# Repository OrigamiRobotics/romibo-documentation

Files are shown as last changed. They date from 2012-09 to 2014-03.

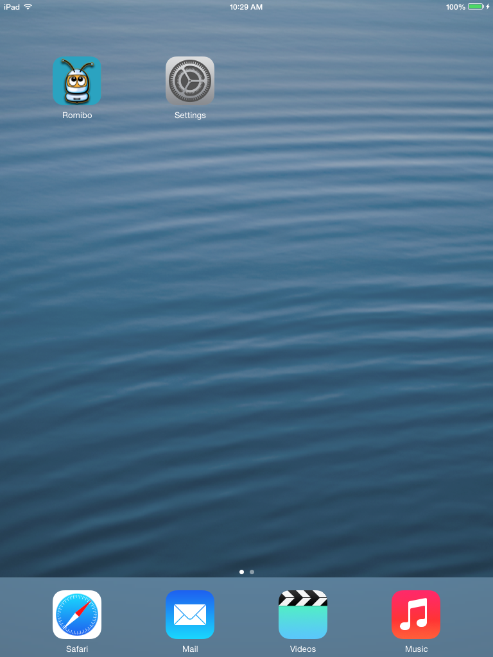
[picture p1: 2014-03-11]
iPad User Guide/Images/IMG_0007.PNG

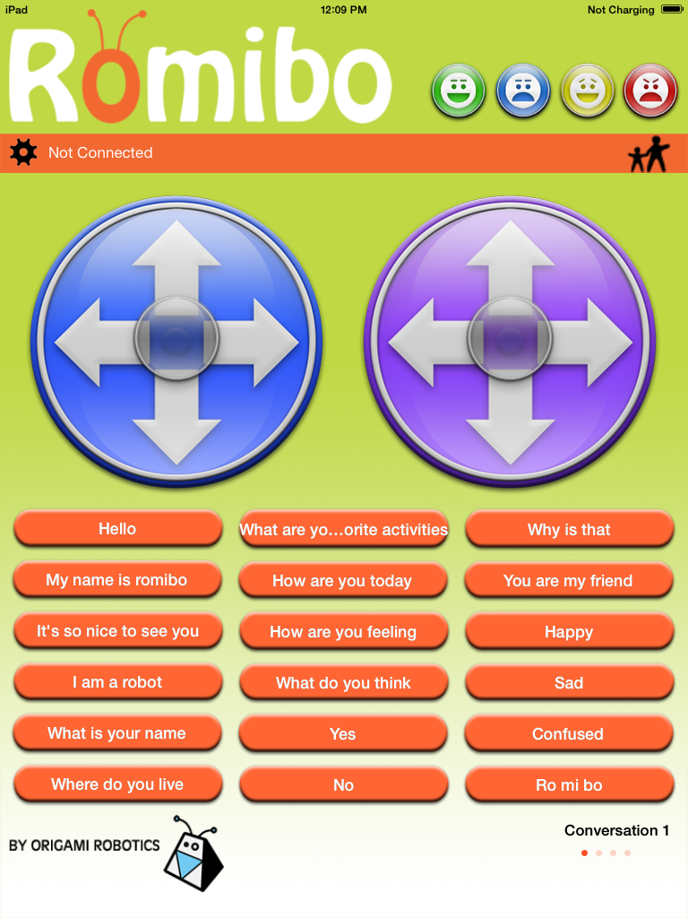
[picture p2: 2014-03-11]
iPad User Guide/Images/IMG_0014.PNG

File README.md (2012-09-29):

romibo-documentation
====================

Repository for documentation and printable materials for the Romibo robot

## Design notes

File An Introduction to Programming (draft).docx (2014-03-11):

An Introduction to Programming with

Romibo and Arduino:

by

Adam Warburton

The following will apply to all programs/sketches found in this tutorial:

// This is free software; you can redistribute it and/or modify

// it under the terms of the GNU General Public License as published by

// the Free Software Foundation; either version 2 of the License, or

// (at your option) any later version.

//

// This is distributed in the hope that it will be useful, but

// WITHOUT ANY WARRANTY; without even the implied warranty of

// MERCHANTABILITY or FITNESS FOR A PARTICULAR PURPOSE. See the

// GNU General Public License for more details.

//

// You should have received a copy of the GNU General Public License

// along with this file; if not, write to the Free Software Foundation,

// Inc., 51 Franklin St, Fifth Floor, Boston, MA 02110-1301 USA

// ##END_LICENSE##

/****************************************************************/

/****************************************************************/

What are Romibo and Arduino anyway?

An Arduino is a single-board microcontroller based on open-source hardware. Essentially an Arduino Board is a small computer that can be programmed to send and receive electrical signals. The Arduino is a computer, just like a laptop or desktop, but instead of being used for word-processing or web-surfing, it can be used in the design of robots and other devices. It also does not have anywhere near the processing power of a desktop computer, but is significantly cheaper and can interact with the physical world. An Arduino board can be programmed through a connection by USB to a computer.

Arduino Boards in themselves can only output weak electrical signals (5 Volts at an approximate maximum of 40 mA). Consequently, the board itself can do little more on its own than turn on LEDs. For this reason, Arduino boards are often connected to shields such as the Romibo Shield.

The Romibo Shield is a board that takes input from the Arduino Board and outputs the appropriate output voltages to the motors, servos, and other components on the Romibo Robot. The Romibo Shield also allows the Arduino to access input from numerous sensors including an accelerometer, microphone, IR sensor, two photo resistors and more. Table 1.1 contains the pins of the Arduino board with names for what they correspond to on the Romibo Shield.

Table 1.1 (modified from Romibo-Arduino-Pin-Assignments.xls by Garthz)

Arduino Pin | Rev3 Signal | Rev3 Function
A1 | RANGE | range sensor input
A2 | PHOTOLEFT | left photosensor input
A3 | PHOTORT | right photosensor input
A4 | PHOTOTOP | top photosensor input
A5 | MIC | microphone signal input
A6 | ENVELOPE | microphone envelope input
A7 | PHOTOFACE | face photosensor input
A8 | LCURRENT | left drive motor current feedback input
A9 | RCURRENT | right drive motor current feedback input
A10 | VINSENSE | battery input voltage input
D2 | FWDLEFT | left drive wheel IN1
D3 | REVLEFT | left drive wheel IN2
D4 | RED | red led PWM
D5 | MOTSLEEP | drive motor sleep output
D6 | MOTFAULT | drive motor fault input
D7 | FWDRT | right drive wheel IN1
D8 | REVRT | right drive wheel IN2
D9 | GRN | green led PWM
D10 | BLUE | blue led PWM
D13 | AUDIOPWM | experimental class-D audio amplifier PWM output
D18 | WIFITX | Serial1 data to WiFi module
D19 | WIFIRX | Serial1 data from WiFi module
D20 | SDA5V | I2C bus data
D21 | SCL5V | I2C bus clock
D28 | TOUCHLEFT | touch switch digital input
D29 | TOUCHBOT | touch switch digital input
D31 | TOUCHTOP | touch switch digital input
D34 | !DACS! | audio SPI chip select out
D35 | DASCK | bit-banged audio SPI clock out
D36 | DASDI | bit-banged audio API data out
D37 | !SPKSHDN | active-high enable for speaker amplifier
D40 | !SDCD! | SD Card detect
D45 | TILTBACK | servo PWM for rear neck servo
D46 | EYE | servo PWM for eyelid servo
D48 | IRIN | IR remote receiver input
D50 | SDDO | hardware SPI for SD Card
D51 | SDDI | hardware SPI for SD Card
D52 | SDSCLK | hardware SPI for SD Card
D53 | SDCS | digital I/O for master-mode SPI

Installing the Arduino IDE

Now that you’ve learned a little about the hardware, now would be a good time to start learning about the software. As stated earlier, the Arduino board can be programmed using a USB port. In order to begin programming with Arduino, you must first install the Arduino IDE on your computer. The Arduino IDE is available free of charge from http://arduino.cc/en/main/software

Please install the version that is appropriate for your device (Windows, Mac, Linux) and then restart your computer if necessary. After a successful installation, you will be able to start the program which should appear similar to that of Figure 1 below.

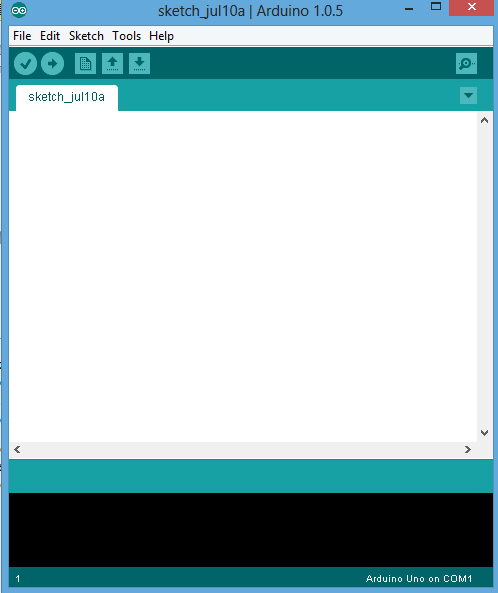
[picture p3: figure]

The first thing you will likely need to do is to change your IDE to work with the Arduino Mega. This is a fairly easy step, simply click Tools and then click on Board in the drop down menu and then choose the Arduino Mega 2560.

Then be sure to plug the robot into the USB port. Then click Tools and then Serial Port. Choose the only serial port available (example COM3). After that you should be ready to start programming.

Program 1:

Your First Sketch - Getting the Robot to Move

The Arduino Community refers to programs as Sketches. This section will guide you through the process of writing sketch that causes the robot to move forward, stop, then repeat. Arduino programming is based off of the open source programming language “Processing”. “Processing” shares similarities with other programming languages such as C++ and Java.

Every Arduino sketch must have two parts:

1. A setup function
2. A loop function

The setup function is self-explanatory. It sets up the Arduino Board. This function is run once and is important because it is used to tell the Arduino which pins to use for input and which to use for output.

The loop function is a function that is run after the setup function. Unlike the setup function however, the loop function will run an infinite number of times. It repeats or loops the function over and over again.

To write the outline of these bits of code, type the following:

void setup()

{

}

void loop ()

{

}

You will notice that the text changes colors. This is to help with programming as different types of code will be different colors. It is very important to keep the capitalization and punctuation the same. Brackets {} are not the same as parenthesis () .

Do not worry too much about the word “void” for now, we will discuss that later. The functions are void because there is no value of a number or character returned by them.

If you typed the code in correctly, it will appear like what is seen in Figure 2 below. Notice that the color of the text turned orange. The space in-between the brackets is where the code for each of the functions will go.

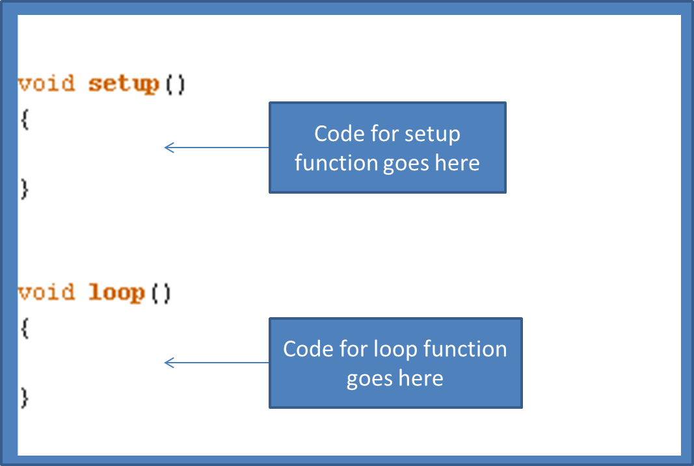
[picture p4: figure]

As mentioned earlier, the setup function will tell the Arduino which pins to use as input and output. For this particular program we will only be using output to the motors. There are four pins which will be important to us. These are Digital Pins 2, 5, 6, and 7.

Pins 2 and 7 tell the left and right motors to move forward respectively.

Pins 5 and 6 correspond to the motor sleep and motor fault switches.

Motor sleep and motor fault may sound foreign to you. Comparing them to every-day life, a person does not simply get into a car, put their foot on the gas and start moving. One has to first turn the key to start the car. One also has to shift gears from park to drive. The motor sleep switch will need to be triggered to essentially start the motor (turn the key). The motor fault switch can be compared to putting the car in drive. To enable these pins, the corresponding pins will first need to be declared as output. To do this, type the following code into the setup function (between the brackets {} after void setup() ).

pinMode (2, OUTPUT);

pinMode (5, OUTPUT);

pinMode (6, OUTPUT);

pinMode (7, OUTPUT);

Note that there is a semicolon “;” after each line. This semicolon tells the compiler (the program on your computer in which you typed this) that you have typed a complete statement. The semicolon is similar to punctuation in speech. Once you finish a statement, you end with a period. Otherwise, sentences would be run-on jumbled messes of difficult to understand nonsensical word jumble that is really really really long, confusing, hard to decipher, and did I mention confusing because if I didn’t I should have.

All joking aside, look at the statements that were typed. Each one of them has the pinMode function. This function tells Arduino that the pin number that follows should be either an input or an output. The number within parenthesis is followed by a comma and then the word INPUT or OUTPUT in all capital letters. The ending parenthesis is then added followed by a semicolon.

Now that we have declared the pins to be outputs, it would be good to set the MOTSLEEP and MOTFAULT pins to output a signal so that we have essentially turned the key to our motors and set them to drive. To do this, type the following code into the setup function (between the brackets) but after the code that set the pins to be outputs.

digitalWrite (5, HIGH);

digitalWrite (6, HIGH);

Again, don’t forget the semicolons! Also, please make sure that the capitalization is correct.

What you’ve just typed is the digitalWrite function. This function is digital because it is outputting to a digital pin (Arduino also has analog pins which will be discussed later). A digital pin is either on or off. To turn a pin on, it is written to as HIGH for a high signal being sent. To turn a pin off it will be sent a LOW signal. Just like the pinMode function, the number used in-between the parenthesis corresponds to the pin that the data is being sent to.

Now that you have successfully set up your Arduino, it’s time to move on to the loop function.

To get the robot to move, you will use the same digitalWrite function that you used to turn the MOTFAULT AND MOTSLEEP switches on. See if you can write these bits of code on your own for pins 2 and 7 in the loop function.

The next function you will need to know about is the delay function. The Arduino board will move through the code you type at an incredibly rapid rate (Thousands of lines per second). To get the board to slow down, you will need to tell it to wait. The delay function has one parameter (value within parenthesis) that tells it how many milliseconds to delay the program. Consequently to have the board wait one second or 1000 milliseconds you should type the function

delay (1000);

This will cause the Arduino to wait a full second before moving onto any code that follows.

As of now, you should have a loop that turns the motors on, waits a second, and then turns the motors on again, then waits another second and so on. But this isn’t especially useful if you want the robot to take a pause for a while. Therefore, you will need to tell the motors to turn off as well. This can be done with the digitalWrite function. Only this time, you will be using LOW instead of HIGH.

digitalWrite (2, LOW);

digitalWrite (7, LOW);

This will turn the motors off after a one second delay. However, the motors will immediately be turned back on again when the loop function repeats. Therefore you should add another delay of a time of your choosing after turning the motors off.

Overall, your program should look something like the following in the compiler.

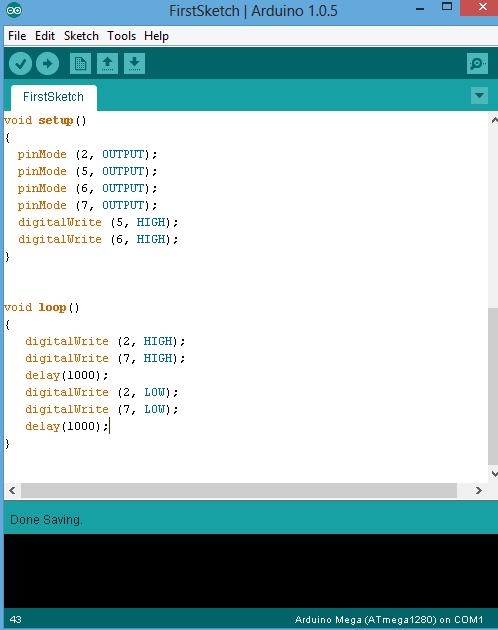
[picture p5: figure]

To check if your program was written with proper syntax, click on the check mark at the top of the program. This will compile your program. This means that it will translate the code you typed into something that can be understood by the Arduino board. If the code is written so that the computer can understand it, the compiler will show a “done compiling” message. Otherwise the compiler will inform you of errors.

Just because a program compiles does not mean it will do what you want it to do. To check to see if your sketch works, you will need to upload it to your Romibo. To do this, connect your Romibo to your computer using a USB cable. Then click on the upload arrow next to the check mark you just used to compile your sketch.

(Depending on your machine, you may have some errors the first time you connect the robot. For help connecting your computer to the Arduino, there are multiple pages on the internet that can be found from your favorite search engine.)

If everything was successful, you will see a message that says “done uploading”. You may now unplug your robot and set it on the floor (away from any obstacles). Turn on the robot and see if it behaves as you expected.

Did the robot do what you expected?

Hopefully it did. If not, there are a few possible reasons it did not. If the robot did not move at all, the motors may not be properly connected or the code may need to be adjusted. The batteries in the robot may also need to be replaced.

Did your robot move backward? If so, the motors were installed backward. This isn’t as huge of a problem as you might expect. One solution is to open the robot and move the motors. The other is to simply alter your program. In the code you can replace the pin numbers you used for the motors to move forward (2 and 7) with the ones for the motors to move in the opposite direction (3 and 8). This is a lot easier than actually opening up the robot, but you may want to note this somewhere if you plan on keeping the robot this way.

Program 2:

Responding to Input:

In this section, you will learn how to make the Romibo Robot respond to input from its touch sensors. The example program will have the robot turn in circles but change direction each time it is triggered by a touch sensor.

As can be seen from the previous table of Arduino pins (table 1.1), the pins for the touch sensors are numbered 28, 29, 30, and 31. Since these pins will be inputting data into the Arduino, these pins will need to be declared as INPUT using the pinMode function.

pinMode ( pinNumber, INPUT);

Make sure to declare all four of these pins in the setup function. To read from a pin you will use the digitalRead() function. The digitalRead function includes one parameter, the pin number that is being read.

digitalRead(28) will return HIGH if the touch sensor/ button is not being pressed and LOW if the button is being pressed. The reason for this is that the button grounds the connection whenever the two pieces of metal come in contact. Simply writing digitalRead(28) as a statement in your code though will do very little. To make the input change something, you will need to instruct your Arduino to make a decision.

One way of allowing your Arduino Board to make a choice is with the “if statement”. An “if statement” asks if something is true, and if it is will do something else. A basic setup of the way to write this “if statement” using normal everyday decisions is:

if (you have a dog)

{

walk it everyday

}

As you can see from the above pseudo-code, the text in the parenthesis is what is being checked to see if it is true. The text in the brackets is what is being done if the checked statement was true. It would not make sense to walk a dog that does not exist.

To check multiple statements you will need to connect the statements with either an || (or) or an && (and). The || or && is text that is understood by the compiler. In pseudo-code

if (you have a dog || you have a cat)

{

put food out

}

This bit of pseudo-code tells you that if you have a dog or if you have a cat that you should put food out for it. You can also give commands for when something isn’t true. For example

if (you have a dog || you have a cat)

{put food out}

else

{

consider getting a pet

}

This “if -else statement” allows the program to choose from two different responses. The “else” is performed whenever the previous if was not performed. From these examples, one “if statement” you will want to form looks something like this:

if (digitalRead(28) == LOW || digitalRead(29) == LOW || digitalRead(30) == LOW || digitalRead(31) == LOW)

{

}

This code will check to see if any of the buttons have been pressed. If so, the code that follows in the brackets will be performed. Notice that there are 2 equal signs to test if something is equal. This is important. One equal sign will actually make something equal to something else. The something that is referred to is a variable. Since this program will be causing the robot to choose between turning right and turning left, we will need to declare a variable to decide which direction the robot is turning.

To declare a Boolean variable named TurningRight that is either true or false we write

boolean TurningRight;

Be sure to put this bit of code at the very top of your Sketch. Being before any of the functions will allow this variable to be accessed anywhere in the sketch. We could have named this variable anything we like (provided it starts with a letter and has no spaces or illegal symbols). However, TurningRight is descriptive of what should be true or false.

To set a variable to some value, you use one equal sign. If you want the robot to turn right at the start of the program, put this bit of code into the setup loop.

TurningRight = true;

This will set the variable to true. Simply doing this though will not cause your robot to turn right. You will have to cause the motors to turn after testing the TurningRight variable. To cause the robot to turn right, you will actually have to tell the left motor to move forward. This is because the right wheel will effectively remain stationary. If you turn to the right yourself, you will notice that you pivot on your right foot and move your left foot around. This is how the robot will have to move as well. This can be visualized with the following image.

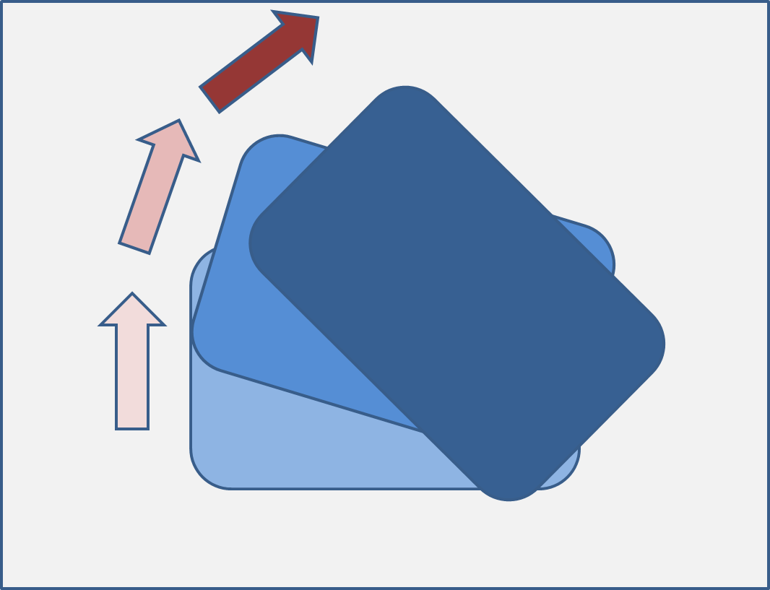
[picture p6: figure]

Given this information about variables, if statements, and input, you should be able to write a complete working sketch that will make the robot change direction when a button is pressed. Give it a try on your own and upload it to the robot. Remember that the left motor forward is pin 2 and the right motor forward is pin 7. If you need help, try searching the internet. For a complete program see the next page.

Hint: “if-else statements” can go within other “if-else statements”

//SecondSketch_Input_

boolean TurningRight;

void setup()

{

TurningRight = true;

pinMode (2, OUTPUT);

pinMode (5, OUTPUT);

pinMode (6, OUTPUT);

pinMode (7, OUTPUT);

digitalWrite (5, HIGH);

digitalWrite (6, HIGH);

pinMode (28, INPUT);

pinMode (29, INPUT);

pinMode (30, INPUT);

pinMode (31, INPUT);

}

void loop()

{

if (digitalRead(28) == LOW || digitalRead(29) == LOW || digitalRead(30) == LOW || digitalRead(31) == LOW)

{

if (TurningRight == true)

{

TurningRight = false;

digitalWrite (2, LOW);

digitalWrite (7, HIGH);

delay (250); //This delay will keep the button from being checked to quickly

}

else

{

TurningRight = true;

digitalWrite (2, HIGH);

digitalWrite (7, LOW);

delay (250); //This delay will keep the button from being checked to quickly

}

}

}

Program 3:

Analog Input, Variable Types, and the Serial Monitor

Up until now, you’ve been using entirely digital input and output. These digital inputs are either completely on or off. However, there is another type of input/output called analog. Use of analog allows there to be a range of values between on and off.

A sensor that is ideal for showing analog input is the photo resistor. If you are unfamiliar with electricity, resistors exist in electrical circuits in order to impede the flow of electrons. Resistors can be thought of as small tunnels that electrons have to pass through. The electrons have to move slower in the same way that cars move slower when entering a tunnel. A photo resistor is a resistor whose resistance (essentially the size of the tunnel) changes whenever a light is shining onto the resistor. A photo resistor’s resistance is less whenever more light is being shined on it. This is because the light essentially loosens the electrons from the material, allowing them to flow easier. (The actual explanation is slightly more complicated. This idea will give you a general idea of the concept however).

The two photo resistors on the front of the Romibo are connected to Analog Pins 2 and 3 for left and right respectively. You may be wondering, “isn’t pin 2 taken already”. The answer is no, digital pin 2 is taken for a motor but analog pin 2 is used for the left photo resistor.

To receive data from the photo resistor, you will need to store it somewhere. Just as you declared a Boolean variable in the last programming exercise, you will also need to declare a variable to store this data. However, this data will not be true/false. The data you will be receiving will be a number. There are multiple ways of storing numbers using Arduino.

Abbreviation | Name | Meaning
int | Integer | Stores integer variables from -32,768 to 32,767
long | Long | Stores larger integer values from -2,147,483,648 to 2,147,483,647
double | Double | Stores values with a decimal point.

The number we will be storing for each photo resistor reading will be an integer. To declare these values you can type:

int leftPhotoReading;

int rightPhotoReading;

Integer values are helpful in storing readings from analog input. They can also be used to save time in remembering values you’d rather not memorize. For example, you’ve been writing to a digital pin 7 to trigger one of the motors for a while now. Instead of writing digitalWrite(7, HIGH), you could define a variable such as FWDRT to 7 and instead type digitalWrite(FWDRT, HIGH). To declare a constant, just type const before the name of the variable and put an equal sign after it followed by the value you want it declared to. For example:

const int FWDRT = 7;

While it is not required, constants are typically typed in all capital letters. To change a non-constant variable, you just type the name of the variable, an equal sign, and then the value you want the variable to change to. The great part about this is that you can make a variable equal to the value returned from a function or a mathematical statement. For example,

int PHOTOLEFT = 2*1-0; // * means multiplication

int PHOTORIGHT = 1 + 4/2;

The compiler will follow order of operations, just like in math class. Therefore the above code will set PHOTOLEFT to 2 and PHOTORIGHT to a value of 3. Instead of assigning values to our reading variables, it will be more useful to allow them to actually read in data from an analog input. To read analog input, use the function analogRead(pin_number). For our code, we will use

leftPhotoReading = analogRead(PHOTOLEFT);

rightPhotoReading = analogRead(PHOTORIGHT);

The analogRead( ) function will return a value from 0 to 1023. For photo resistors, the brighter the light shining on the photo resistor, the lower the number returned.

To see what numbers are being returned by your robot you can use a tool called the Serial Monitor. To have your robot return data back to your computer, you will have to include a few lines of code. In your setup loop please include

Serial.begin(9600);

For your loop() please include the following. Be sure that you declare all of the necessary variable and set the correct pinMode for all pins. For a working program see Program3 SerialPrint Example.

leftPhotoReading = analogRead(PHOTOLEFT);

rightPhotoReading = analogRead(PHOTORIGHT);

Serial.print("leftPhotoReading ");

Serial.println(leftPhotoReading);

Serial.print("rightPhotoReading ");

Serial.println(rightPhotoReading);

delay(300);

After successfully compiling your program, upload it to your robot. Do not unplug the USB port. Instead, click on Tools at the top of your Arduino IDE. Then click on Serial Monitor. Be sure that AutoScroll is checked, both NL & CR is chosen from the first drop down list, and 9600 baud is selected. Cover and shine lights on the photo resistors to see how the data responds. Look back at the code you entered to see how the Serial.print and Serial.println functions work.

Notice that parenthesis output the exact text and that variable names output the variable value.

//Program3 SerialPrint Example

int leftPhotoReading;

int rightPhotoReading;

const int PHOTOLEFT = 2;

const int PHOTORIGHT = 3;

void setup()

{

Serial.begin(9600);

}

void loop()

{

leftPhotoReading = analogRead(PHOTOLEFT);

rightPhotoReading = analogRead(PHOTORIGHT);

Serial.print("leftPhotoReading ");

Serial.println(leftPhotoReading);

Serial.print("rightPhotoReading ");

Serial.println(rightPhotoReading);

delay(300);

}

Now, that you’ve seen how the analogRead function works with photo resistors, you are ready to start making more complex programs. Instead of the program you made in the last section that has the robot change direction by a button press, try making one that has the robot follow a light. Review the section of if-else statements if need be. The following are available to produce true or false values. You have seen == before, the other should be easy to infer.

> greater than < less than >= greater than or equal to <= less than or equal to == equal to

Between, these comparisons and the ability to use +,-,*,and / to add, subtract, multiply, and divide, you should be able to make your robot do more complex motions. Example code of a robot following a light can be found on the following page. Try to create your own or edit the one provided to fine tune your program.

//Program3 ChaseLight Example

int leftPhotoReading;

int rightPhotoReading;

const int PHOTOLEFT = 2;

const int PHOTORIGHT = 3;

const int FWDRT = 7;

const int FWDLEFT = 2;

void setup()

{

pinMode (2, OUTPUT);

pinMode (5, OUTPUT);

pinMode (6, OUTPUT);

pinMode (7, OUTPUT);

digitalWrite (5, HIGH);

digitalWrite (6, HIGH);

}

void loop()

{

leftPhotoReading = analogRead(PHOTOLEFT);

rightPhotoReading = analogRead(PHOTORIGHT);

if(leftPhotoReading < rightPhotoReading - 30)

{

digitalWrite(FWDRT, HIGH);

digitalWrite(FWDLEFT, LOW);

}

else if(rightPhotoReading < leftPhotoReading - 30)

{

digitalWrite(FWDRT, LOW);

digitalWrite(FWDLEFT, HIGH);

}

else

{

digitalWrite(FWDRT, HIGH);

digitalWrite(FWDLEFT, HIGH);

}

}

Program 4:

Analog Output, Lighting, Changing Speeds, and Loops

In the last section, we covered Analog Input which had a range of values from 0 to 1023. Analog output is similar but it will only be able to use values from 0 to 255. Consequently, an effective way to convert from one to the other is to divide by four. Using the value of 255 will cause the pin to be constantly on while 0 will make it constantly off. A value in between will cause the pin to be on a fraction of the time. The function to use for analog output is

analogWrite(pinNumber, value); //where ‘value’ is from 0 to 255

This function will typically be used in void loop() section of the code. Analog Output is an effective way to cause the motors to change speeds or to cause the LED lights to appear to be at different brightness levels. The Romibo has a Tri-color LED which creates the color in the antenna. While the LED is tri-color it can actually create any other color from its three colors (red, green, and blue). You are likely familiar with the three primary colors when painting, red, yellow, and blue. From these three paint colors you can mix any other color of paint. Light is similar but the three primary colors are different. For light, they are red, green, and blue. These same three colors are the ones used in LCD TVs and monitors to create every color on the screen.

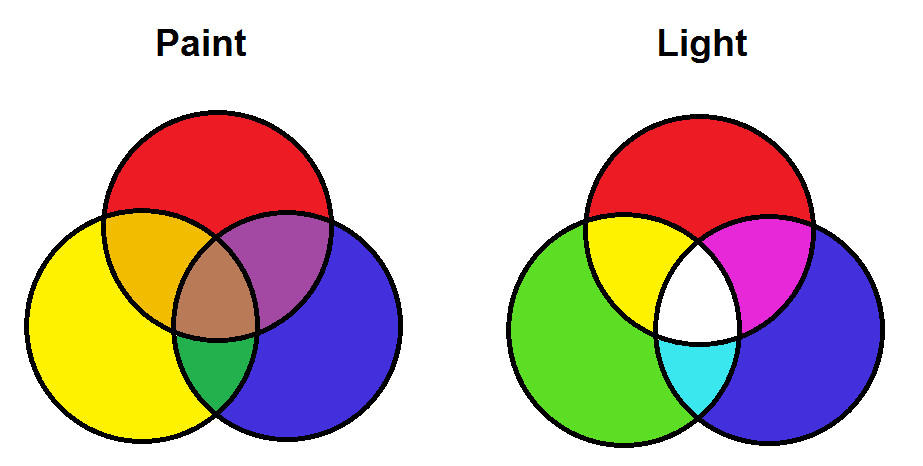
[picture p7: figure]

The reason for the difference in the primary colors is that when you add paint colors together, you are actually subtracting out the wavelengths of light that are reflected. When you add more light to something, you are adding the colors together. As you add more paint color, the color gets darker. But when you add more light, everything gets lighter.

The pins for the Red, Green, and Blue parts of the LED on Romibo are 4, 9, and 10 respectively. While these are considered digital pins, they will still accept a command from analogWrite(pin, val);

If you plan on changing the value sent to a pin gradually, it will likely be beneficial to use something called a loop in programming. You have actually been using an infinite loop all along with the loop function. However, these loops will be performed within your code if some condition is true. The three loops introduced are found in other languages such as C++ and javascript as well.

The first loop we may use is a “for” loop. A for loop will loop a certain number of times. Rather it will repeat a particular set of code a certain predetermined number of times. If you wanted to make the LED’s Blue output gradually increase, you could use the following code.

for (int i = 0; i < 254; i++)

{

analogWrite(10, i); //code that is repeated each time

delay (4);

}

In this example, the variable ‘i’ is declared inside of the parenthesis. It will continue as long as the next statement is true (i < 254;). The update condition is then placed after that (i++ means that ‘i’ will increase by one each time). After parenthesis, the code that is repeated follows inside brackets (just like the if statement). Notice, that since ‘i’ increases each time the loop repeats, that the value written to the blue led will increase each time the loop repeats. This variable ‘i’ will not exist after the for loop as it is a local variable.

This loop is very helpful, but what if you don’t know how many times you want the loop to repeat? You could make a loop that repeats as long as an input button is pressed for instance, or as long as the photo resistor receives light of a certain brightness. A good loop to use would be a while loop.

int outputValue = 0;

while (analogRead(PHOTORIGHT) > 400)

{

outputValue = analogRead(PHOTORIGHT)/4;

analogWrite(10, outputValue); //code that is repeated each time

}

Notice that the code will repeat until analogRead(PHOTORIGHT) is less than or equal to 400. This could be dangerous to use if the value will never fall that low. The value output to the Blue LED pin will change constantly but no other code in your program will be executed until you leave the while loop.

A loop that is similar to the while loop but will be executed at least one time is the do-while loop.

int outputValue = 0;

do

{

outputValue = analogRead(PHOTORIGHT)/4;

analogWrite(10, outputValue); //code that is performed at least once

} while (analogRead(PHOTORIGHT) > 400);

This loop will perform the code inside the brackets at least once regardless of whether analogRead(PHOTORIGHT) is greater than 400 or not. If that is false, the program will continue on as normal, having updated the Blue LED pins value. An example program that will let you see the colors of light changing follows. Try it on your Romibo and edit it to your liking.

//Antenna Color Shift

int timer = 0;

const int RED = 4;

const int BLUE = 10;

const int GRN = 9;

void setup()

{

pinMode (RED, OUTPUT);

pinMode (GRN, OUTPUT);

pinMode (BLUE, OUTPUT);

}

void loop()

{

timer = 0;

while (timer < 254)

{

analogWrite(RED, timer);

timer++;

delay (4);

}

for (int i = 0; i < 254; i++)

{

analogWrite(RED, timer - i);

analogWrite(BLUE, i);

delay (4);

}

timer = 0;

do

{

analogWrite(BLUE, 254 - timer);

analogWrite(GRN, timer);

timer++;

delay(4);

}while (timer < 253);

while (timer > 0)

{

analogWrite(GRN, timer);

timer--;

delay(3);

}

}

Other Example Programs:

This manual is a work in progress. There are more lessons to come. Some other example programs follow if you’d like to experiment with them.

//Read IR Values

const int IRIN = 48;

const int RED = 4;

const int BLUE = 10;

const int GRN = 9;

int highPulse;

int lowPulse;

const int RESOLUTION = 20;

int pulses[60][2];

long useconds;

int currentPulse;

void setup(void)

{

pinMode (RED, OUTPUT);

pinMode (GRN, OUTPUT);

pinMode (BLUE, OUTPUT);

pinMode (IRIN, INPUT);

Serial.begin(9600);

Serial.println("Printing IR delays");

}

void loop(void)

{

currentPulse = 0;

while (digitalRead(IRIN))

{

while (digitalRead(IRIN))

{

useconds = useconds + RESOLUTION;

delayMicroseconds(RESOLUTION);

}

pulses[currentPulse][0] = useconds;

useconds = 0;

while (!digitalRead(IRIN))

{

useconds = useconds + RESOLUTION;

delayMicroseconds(RESOLUTION);

if (useconds > 4800)

break;

}

pulses[currentPulse][1] = useconds;

currentPulse++;

}

Serial.println("New Data Set");

for (int i = 0; i < currentPulse; i++)

{

Serial.print(pulses[i][0]);

Serial.print(" ");

Serial.print(pulses[i][1]);

Serial.println(" ");

}

//Respond to IR Values

//Works with Sanyo Remote to trigger lights

const int IRIN = 48;

const int RED = 4;

const int BLUE = 10;

const int GRN = 9;

int highPulse;

int lowPulse;

const int RESOLUTION = 20;

int pulses[60][2];

long useconds;

int currentPulse;

boolean lighton = false;

void setup(void)

{

pinMode (RED, OUTPUT);

pinMode (GRN, OUTPUT);

pinMode (BLUE, OUTPUT);

pinMode (IRIN, INPUT);

Serial.begin(9600);

Serial.println("Printing IR delays");

}

void loop(void)

{

currentPulse = 0;

while (digitalRead(IRIN))

{

while (digitalRead(IRIN))

{

useconds = useconds + RESOLUTION;

delayMicroseconds(RESOLUTION);

}

pulses[currentPulse][0] = useconds;

useconds = 0;

while (!digitalRead(IRIN))

{

useconds = useconds + RESOLUTION;

delayMicroseconds(RESOLUTION);

if (useconds > 4800)

break;

}

pulses[currentPulse][1] = useconds;

currentPulse++;

}

Serial.println("New Data Set");

for (int i = 0; i < currentPulse; i++)

{

Serial.print(pulses[i][0]);

Serial.print(" ");

Serial.print(pulses[i][1]);

Serial.println(" ");

}

for (int i = 0; i < 90; i++)

{

if (pulses[i][0] == 840 && pulses[i+1][0] == 840 && pulses[i+2][0] == 840 && pulses[i+3][0] == 840 && pulses[i+4][0] == 1740 && pulses[i+5][0] == 840);

{

lighton = !lighton;

if (lighton)

{

digitalWrite(GRN, HIGH);

digitalWrite(RED, LOW);

digitalWrite(BLUE, LOW);

}

else

{

digitalWrite(GRN, LOW);

digitalWrite(RED, LOW);

digitalWrite(BLUE, LOW);

}

break;

}

if (pulses[i][0] == 840 && pulses[i+1][0] == 840 && pulses[i+2][0] == 840 && pulses[i+3][0] == 860 && pulses[i+4][0] == 840 && pulses[i+5][0] == 1720);

{

lighton = !lighton;

if (lighton)

{

digitalWrite(GRN, LOW);

digitalWrite(RED, HIGH);

digitalWrite(BLUE, LOW);

}

else

{

digitalWrite(GRN, LOW);

digitalWrite(RED, LOW);

digitalWrite(BLUE, LOW);

}

break;

}

if (pulses[i][0] == 1720 && pulses[i+1][0] == 1740 && pulses[i+2][0] == 1720 && pulses[i+3][0] == 1740);

{

lighton = !lighton;

if (lighton)

{

digitalWrite(GRN, LOW);

digitalWrite(RED, LOW);

digitalWrite(BLUE, HIGH);

}

else

{

digitalWrite(GRN, LOW);

digitalWrite(RED, LOW);

digitalWrite(BLUE, LOW);

}

break;

}

}

}

For some, programming can easily be learned from simply reading over someone else’s work. The following program was written with the QoLT young scholars program. Try uploading the code to your robot to see how it behaves. Refer back to the code to see why it does each behavior. Be sure to touch each of the touch sensors.

// From_Scratch_Demo

// Anna + Jason + Adam

//These includes include other files for programming.

//These files tell the arduino how to handle functions that involve a timer or servos.

#include <Timer.h>

#include <Servo.h>

//The following are variables.

//int stands for integer. The name that follows is the name of the variable.

//These variables can hold integer values.

int inversedistance;

int beat1time;

int beat2time;

int beat3time;

int beat4time;

int beataveragetime;

//The const before the int means that the variable is a constant

//These values will not change while the program is running.

const int FWDLEFT = 2; //These Numbers are the numbers of the pins on the arduino board that connect to the motors.

const int REVLEFT = 3; //For Example, sending a signal to REVLEFT (pin 3) will cause the Left motor to move in reverse.

const int FWDRT = 7; //It is not necessary to declare these constants if you remember the pins. But since that would be difficult the variables can stand in place for the pin numbers later.

const int REVRT = 8;

const int RANGEPIN = 1;

//A boolean variable is either true or false; The value can be declared initially with =

//The robot will not start dancing until code instructs it to do so.

boolean IsDancing = false;

int BeatsDanced = 0;

boolean lastButton = true;

boolean motorOn = false;

//A long is also an integer but it is for larger numbers.

//Since time is measured in milliseconds, these values can become quite large. Therefore long is more appropriate than int.

long startTime;

//Servo is for use with Servo Motors. These will move to a particular position.

Servo ForwardServo;

Servo BackwardServo;

//This is a function declaration. void means that the variable has no parameters

//It is neither true, false, a number, or a letter. It is nothing really.

void DanceFunction (void);

//This setup function is required for use with arduino.

//Anything that follows in the squiggly brackets {} will be performed when the robot is first turned on.

void setup(void)

{

Serial.begin(9600);

ForwardServo.attach(44);

BackwardServo.attach(45);

//lets motors work

pinMode (5, OUTPUT);

digitalWrite (5, HIGH);

pinMode (6, OUTPUT);

digitalWrite (6, HIGH);

delay (1000);

}

//This loop function is also required for use with arduino

//After setup is performed, loop will be performed.

//The loop function will repeat over and over again until the robot is turned off.

void loop()

{

if (digitalRead (28) == LOW)

{

ForwardServo.writeMicroseconds(2000); //tilts head forward

BackwardServo.writeMicroseconds(2000);

delay(1000);

ForwardServo.writeMicroseconds(1000); //tilts head backward

BackwardServo.writeMicroseconds(1000);

delay(1000);

ForwardServo.writeMicroseconds(1500); //tilts head to center

BackwardServo.writeMicroseconds(1500);

delay(500);

}

if (digitalRead (29) == LOW)

{

digitalWrite (FWDLEFT, HIGH);

delay (1000);

digitalWrite (FWDLEFT, LOW);

digitalWrite (REVLEFT, HIGH);

delay (1000);

digitalWrite (REVLEFT, LOW);

}

if (digitalRead (31) == LOW)

{

digitalWrite (FWDRT, HIGH);

delay(1000);

digitalWrite (FWDRT, LOW);

digitalWrite (REVRT, HIGH);

delay(1000);

digitalWrite (REVRT, LOW);

}

//DanceFunction();

if (digitalRead(30) == LOW && lastButton == true)

{

startTime = millis();

digitalWrite (FWDLEFT, HIGH);

digitalWrite (FWDRT, HIGH);

ForwardServo.writeMicroseconds(2000); //tilts head forward

BackwardServo.writeMicroseconds(2000);

lastButton = false;

delay(150);

motorOn = true;

}

if ((digitalRead(30) == LOW && lastButton == false) || (millis() - startTime >= 30000))

{

digitalWrite (FWDLEFT, LOW);

digitalWrite(FWDRT, LOW);

lastButton = true;

delay(150);

motorOn = false;

}

if (motorOn == true && analogRead(RANGEPIN) >= 260)

{

digitalWrite(FWDLEFT, LOW);

digitalWrite(FWDRT, LOW);

if (millis() % 2)

{ digitalWrite(REVLEFT, HIGH);

digitalWrite(REVRT, HIGH);

delay(200);

digitalWrite(REVLEFT, LOW);

delay(1000);

digitalWrite(REVRT, LOW);

}

else

{

digitalWrite(REVLEFT, HIGH);

digitalWrite(REVRT, HIGH);

delay(200);

digitalWrite(REVRT, LOW);

delay(1000);

digitalWrite(REVLEFT, LOW);

}

}

if (motorOn == true && analogRead(RANGEPIN) <=230)

{

digitalWrite(FWDLEFT, HIGH);

digitalWrite(FWDRT, HIGH);

}

Serial.println(analogRead(RANGEPIN));

inversedistance = analogRead(RANGEPIN);

if (inversedistance >= 230)

{

ForwardServo.writeMicroseconds(1000); //tilts head backward

BackwardServo.writeMicroseconds(1000);

}

if (inversedistance <=210)

{

ForwardServo.writeMicroseconds(1500); //tilts head to center

BackwardServo.writeMicroseconds(1500);

}

}

void DanceFunction (void)

{

if (digitalRead (30) == LOW)

{

beat1time = millis();

delay (180);

for (int i=0; i < 1000; i++)

{

if (digitalRead(30) == LOW)

{

beat2time = millis();

i=1000;

}

delay (2);

}

delay (180);

for (int i=0; i < 1000; i++)

{

if (digitalRead(30) == LOW)

{

beat3time = millis();

i=1000;

}

delay (2);

}

delay (180);

for (int i=0; i < 1000; i++)

{

if (digitalRead(30) == LOW)

{

beat4time = millis();

i=1000;

delay(180);

}

delay (2);

}

beataveragetime = (((beat2time - beat1time) + (beat3time - beat2time) + (beat4time - beat3time))/3);

IsDancing = true;

}

if (IsDancing)

{

ForwardServo.writeMicroseconds(1800); //tilts head forward

BackwardServo.writeMicroseconds(1800);

digitalWrite (FWDLEFT, HIGH);

digitalWrite (REVRT, HIGH);

delay(beataveragetime/6);

digitalWrite (FWDLEFT, LOW);

digitalWrite (REVRT, LOW);

delay(beataveragetime/6);

delay(beataveragetime/3);

ForwardServo.writeMicroseconds(1200); //tilts head backward

BackwardServo.writeMicroseconds(1200);

digitalWrite (FWDRT, HIGH);

digitalWrite (REVLEFT, HIGH);

delay(beataveragetime/6);

digitalWrite (FWDRT, LOW);

digitalWrite (REVLEFT, LOW);

delay(beataveragetime/6);

BeatsDanced++;

if (BeatsDanced >= 16)

{

BeatsDanced = 0;

IsDancing = false;

}

}

}

I hope that you’ve enjoyed this introduction to programming with Romibo and Arduino. There is always more to learn. For other code, check out Romibo’s github page. For information on programming with Arduino, there are numerous resources on Arduino.cc/en

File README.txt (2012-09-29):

README.txt
September 28, 2012

This folder contains documentation on the Romibo(R) robot, a
social robot designed for therapy, education and fun.

The Romibo Project is a Carnegie Mellon University research project and a
community co-development project managed by Origami Robotics LLC.  More project
information can be found at http://www.romibo.org. Romibo is a registered
trademark of Origami Robotics LLC.

================================================================ 

The mechanical design drawings were created by Garth Zeglin using the commercial
CAD program SolidWorks 2010 Standard.

The CAD model primarily includes the flat snap-fit plastic parts of the robot
structure.  These are suitable for laser-cutting from flat double-smooth ABS
plastic of nominal 1/8" thickness.  This material has an actual thickness of
about 0.118 inches, reflected in the slot widths in the structure.

All mechanical files are available under the terms of the GNU General Public
License Version 2, the text of which appears in
GNU-General-Public-License-Version-2.txt.

The full notice for each file is as follows:

    Copyright (C) 2012 Carnegie Mellon University.

    This program is free software; you can redistribute it and/or modify
    it under the terms of the GNU General Public License as published by
    the Free Software Foundation; either version 2 of the License, or
    (at your option) any later version.

    This program is distributed in the hope that it will be useful,
    but WITHOUT ANY WARRANTY; without even the implied warranty of
    MERCHANTABILITY or FITNESS FOR A PARTICULAR PURPOSE.  See the
    GNU General Public License for more details.

    You should have received a copy of the GNU General Public License along
    with this program; if not, write to the Free Software Foundation, Inc.,
    51 Franklin Street, Fifth Floor, Boston, MA 02110-1301 USA.

Note that this license is applied under the theory that a CAD file is "source
code" which is compiled into "object code" in the form of a plot file, drawing,
laser cutter file, or fabricated object.  In particular, if you distribute any
changes to the design, you must also include any changes to CAD files.  This
note does not supersede any terms of the license.

The Romibo(R) name is trademarked by Origami Robotics, LLC, and is not itself
available under this license.

The following files are Copyright (c) 2012 Carnegie Mellon University and available under GPL 2:

  Romibo-eyelid-template.pdf
  Romibo-laser-cutting-plan.dxf
  Romibo-laser-cutting-plan.pdf
  Romibo-structural-assembly.pdf

================================================================

The electronic design drawings for the controller board were created by Garth
Zeglin using the commercial CAD program EAGLE 5.10.0.  The controller is a
"shield" which fits a standard Arduino Mega microcontroller.  The board design
includes all I/O for the Romibo robot.  User-friendly documentation is located
separately in the romibo-documentation package.

All electronic files are available under the terms of the GNU General Public
License Version 2, the text of which appears in
GNU-General-Public-License-Version-2.txt.

The full notice for each file is as follows:

    Copyright (C) 2012 Origami Robotics LLC.

    This program is free software; you can redistribute it and/or modify
    it under the terms of the GNU General Public License as published by
    the Free Software Foundation; either version 2 of the License, or
    (at your option) any later version.

    This program is distributed in the hope that it will be useful,
    but WITHOUT ANY WARRANTY; without even the implied warranty of
    MERCHANTABILITY or FITNESS FOR A PARTICULAR PURPOSE.  See the
    GNU General Public License for more details.

    You should have received a copy of the GNU General Public License along
    with this program; if not, write to the Free Software Foundation, Inc.,
    51 Franklin Street, Fifth Floor, Boston, MA 02110-1301 USA.

Note that this license is applied under the theory that a CAD file is "source
code" which is compiled into "object code" in the form of a plot file, drawing,
or fabricated object.  In particular, if you distribute any changes to the
design, you must also include any changes to CAD files.  This note does not
supersede any terms of the license.

The Romibo(R) name is trademarked by Origami Robotics, LLC, and is not itself
available under this license.

The following files are Copyright (c) 2012 Origami Robotics LLC and available under GPL 2:

  RomiboShieldRev3-bottom-component-placement.pdf
  RomiboShieldRev3-bottom-view.pdf
  RomiboShieldRev3-circuit-schematic.pdf
  RomiboShieldRev3-top-component-placement.pdf
  RomiboShieldRev3-top-view.pdf

================================================================

Also included are text documents describing the assembly, use, and modification
of the Romibo robot.  All files are provided under the copyright of their
respective authors under a Creative Common Attribution-NonCommercial-ShareAlike
license.

The full license text appears in Creative-Commons-BY-NC-SA-3.0.html

For more details on the license: http://creativecommons.org/licenses/by-nc-sa/3.0/

================================================================

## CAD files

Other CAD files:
Romibo-laser-cutting-plan.dxf

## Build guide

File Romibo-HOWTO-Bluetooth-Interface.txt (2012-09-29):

Romibo HOWTO Guide - Using a Romibo(R) Rev3 with a Bluetooth Modem

Copyright (c) 2012 Garth Zeglin
Provided under the terms of the Creative Common Attribution-NonCommercial-ShareAlike license.

================================================================
History.

Sep 29, 2012 - reformatted as plain text (emacs org-mode).
Sep 20, 2012 - original version by Garth Zeglin.

================================================================
Legal.

The Romibo(R) robot is a social robot designed for therapy, education and fun.
The Romibo Project is a Carnegie Mellon University research project and a
community co-development project managed by Origami Robotics LLC.  More project
information can be found at http://www.romibo.org. Romibo is a registered
trademark of Origami Robotics LLC.

================================================================

1. Introduction.

   The Romibo Rev3 board exposes an RS-232 serial port on a connector which can
   connect to an external Bluetooth module for remote control from a host such as a
   laptop.  This page details the hardware and software details for setting this
   up.

2. BlueSMiRF Silver

   We have tested the following Bluetooth module with Romibo:

   Bluetooth Modem - BlueSMiRF Silver
   SparkFun part WRL-10269 
   $39.95/each
   https://www.sparkfun.com/products/10269

   The module is a carrier board for a Roving Network RN-42 module.  The
   "Sparkfun page":https://www.sparkfun.com/products/10269 has documentation
   including schematic and RN-42 users guide.

3. Preparing the BlueSMiRF

   The module has a row of six pads at one edge.  We use just the middle four.  Our preparation:

     1. Solder a four-pin Molex connector to the middle four pins of the BlueSMiRF
        on the component side of the module.  The connector part is Molex
        22-12-2044, available from Mouser as 538-22-12-2044.  This is the
        right-angle version of the J1 serial port connector on the Romibo Rev3
        board (labeled "WiFi").
     2. On the back of the BlueSMiRF, solder across the CTS/RTS bridge pads. They
        are unlabeled, but close to the "n" in "sparkfun.com".
     3. Make a four-wire cable. The cable uses two identical housings, Molex
        22-01-3047 (Mouser 538-22-01-3047), and a total of eight crimp pins, Molex
        08-52-0123 (Mouser 538-08-52-0123).  The wiring must follow the following
        pattern:

        J1 on Rev3       signal                           BlueSMiRF Molex
        A connector                                       B connector        
        1                +3.3V                            4                
        2                TX (Arduino -> Bluetooth)        1
        3                RX (Bluetooth -> Arduino)        2
        4                GND                              3

        Label the Arduino end "A" and the Bluetooth end "B" and always use it in this orientation.

4. Pairing the BlueSMiRF with a laptop.

   All Bluetooth devices must be "paired" with a host to allow a connection.  The
   details vary with operating system.  Following is a result from testing on two
   Mac laptops:

     1. Plug the BlueSMiRF "A" cable end into the Rev3 board.  Plug the Arduino
        into USB to provide power.
     2. A PowerBook G4 running OS X 10.4 failed to pair with the Bluetooth device.
     3. A MacBook Pro running OS X 10.6 promptly discovered it as RN42-45E3.
     4. Select "Passcode Options" and "Do not use a passcode"
     5. It paired as device /dev/tty.RN42-45E3-SPP
     6. On first connection it requested a pairing code.  The code 1234 worked.

5. Setting up Romibo for Bluetooth Access

  The J1 connector uses Arduino Serial Port 1, available in software as the
  Serial1 object.  Serial Port 0 is the USB connection and is available as the
  Serial object.

  Some of the default sketches implement a command processor to parse input from
  Serial1.  Things to check:

    1. The top-level sketch should initialize the port with a baud rate, typically
       in setup.  E.g. Serial1.begin(115200); The default BlueSMiRF baud rate is
       115200, it isn't clear if that can be changed via the normal host driver.

    2. The command line processor should be enabled, typically in CommandLine.ino.
       The function poll_network_input() needs to be called.  It is enabled by the
       configuration value ROMIBO_WIFLY_INSTALLED.  Check for this value in the
       RomiboConfig.h file and make sure it is set to 1.  This function is called
       from the core robot polling loop in RomiboRobot.cpp.

    3. The command protocol is ASCII and line-delimited.  The best documentation
       is the code in CommandLine.ino.

    4. Romibo will ignore commands over Bluetooth until a "begin" command is
       received.

    5. Others to try: set, drive, stop, say, etc.

    6. Additional commands can be added at will into the if/else structure in
       execute_command().

    7. There is not yet implemented any text output to Serial1(), so output
       commands will work but no sensors can be read.  This is not hard, but will
       involve adding commands to generate output to Serial1.  It is recommend to
       also use the Arduino IDE serial console while debugging.

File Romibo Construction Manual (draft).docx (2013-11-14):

Romibo Construction Manual

Valentin Darre and Adam Warburton

Part 1: Head Construction

Materials Needed:

- Plastic Romibo Parts (20 – blinking eyelids model) (16 – earlier model)
- Phillips Screwdrivers (2) (Size 1 and Size 00)
- Screws (18) (various size)
  - 4 Servo (s2)
  - 4 Satellite Boards (s3)
  - 2 Servo Arm (s1)
  - 8 Switches (s4)
- Wi-Fly Board
- Satellite Boards (2)
- Touch Switches (4)
- Fiber Optic Cables (2)
- Rubber Rings (4)
- Resistor Servo HS-485HB (Servo)
- Eye Strut (L)
- Wire (J)
- Paper Eyelids

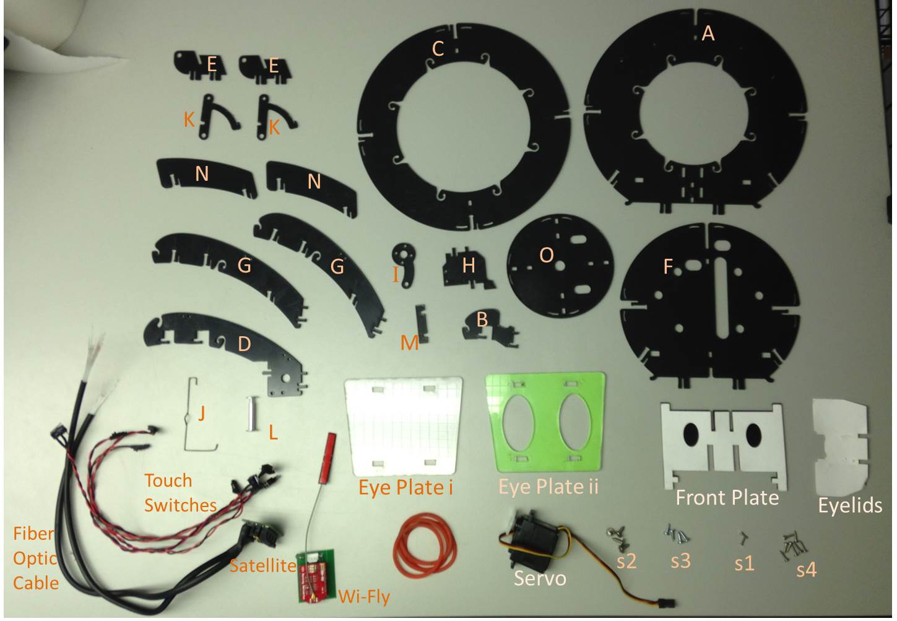
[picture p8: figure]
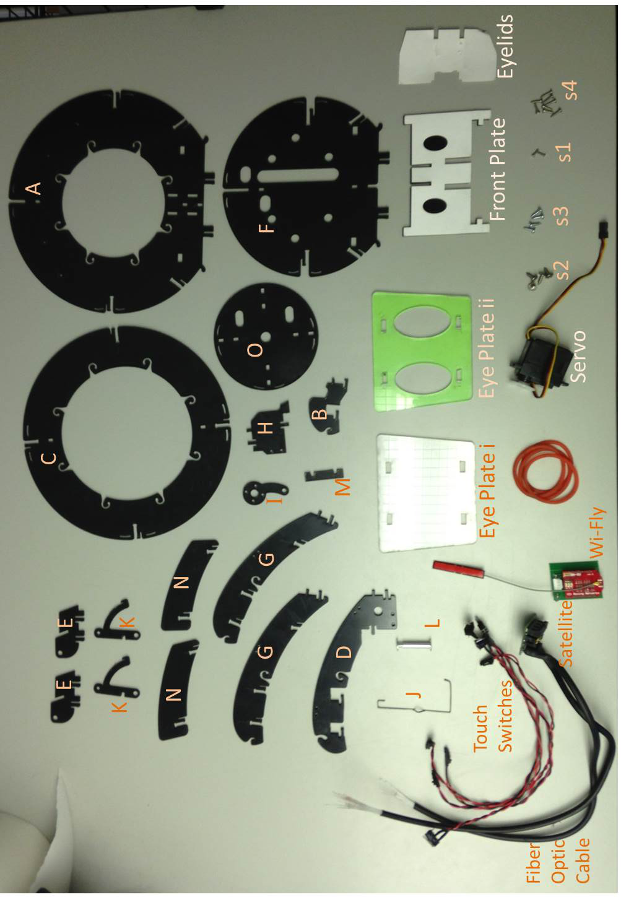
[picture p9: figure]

Time Needed: 30 Minutes

Steps:

Connect Part A to Part B

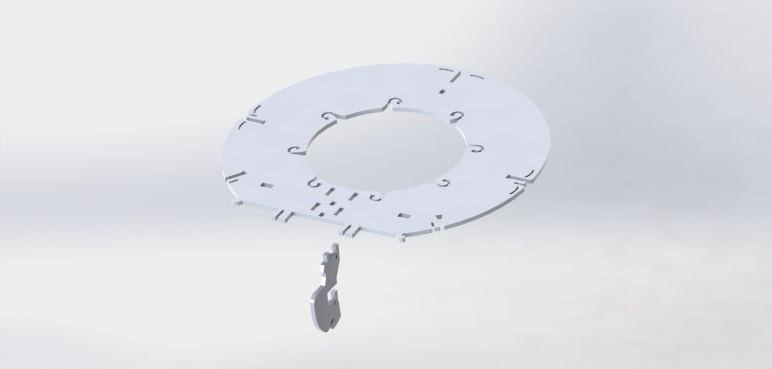
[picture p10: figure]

Connect Part C to Part B

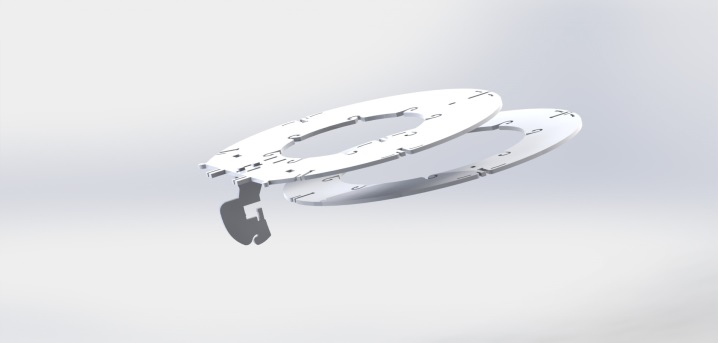
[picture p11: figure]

Connect Part D to Parts A and C

Connect 2 of part E to Part A

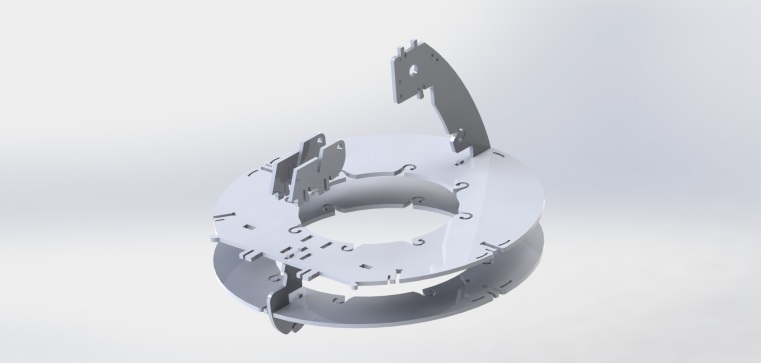
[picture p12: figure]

Connect Part F to Part D

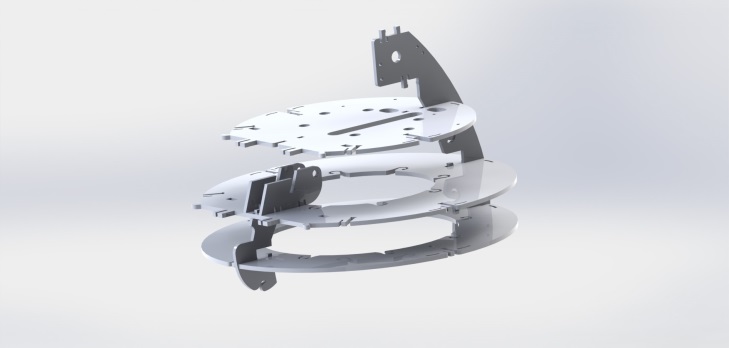
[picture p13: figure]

Connect 2 of Part G to either side.

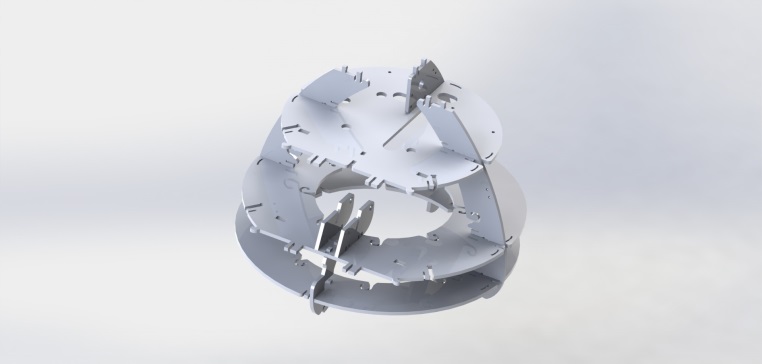
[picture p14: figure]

E

Connect Part H to Part F

Make sure that white plastic wheel is centered.

Put Servo Arm (I) on the Servo

With Servo facing you, and the cable to the right, attach the servo arm facing down.

Use two screws (s1) to attach arm.

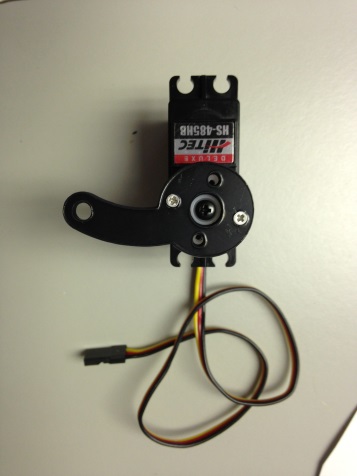
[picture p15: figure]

Place Servo on top with arm going through opening.

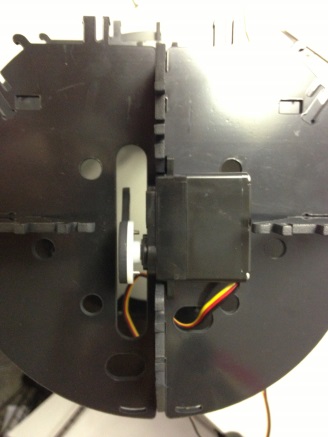
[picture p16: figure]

Screw Servo In (s2)

Insert Metal Wire (J) through Servo Arm hole (I).

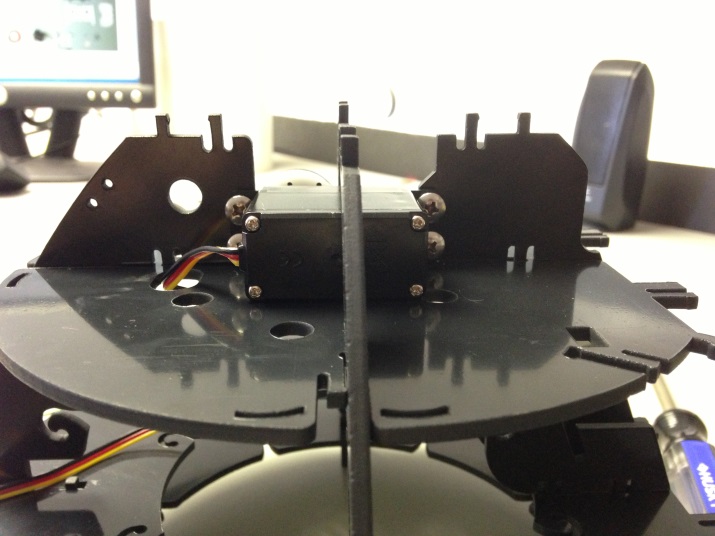
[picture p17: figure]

Slide Parts K around Wire (J)

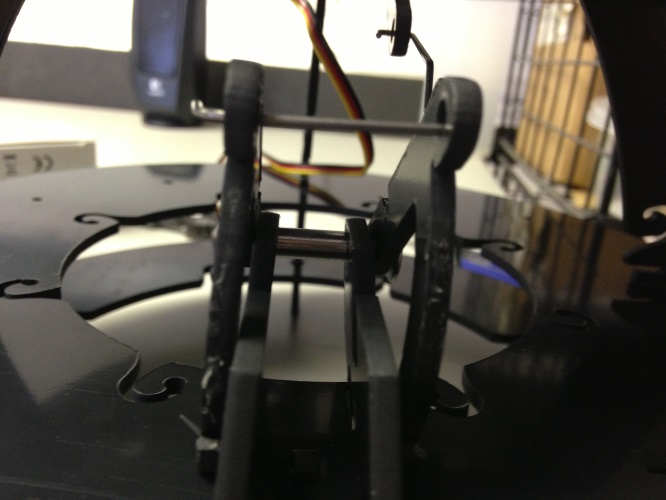
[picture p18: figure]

Feed Eye Strut (L) through Bottom hole of parts K and hole in part E.

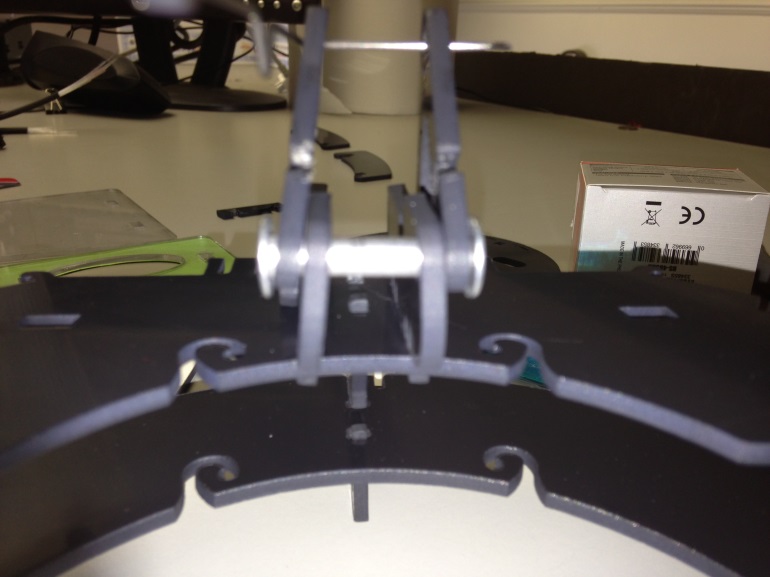
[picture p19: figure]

Attach Part M to back part of both K pieces.

Gently push Eyelid Mechanism all the way back.

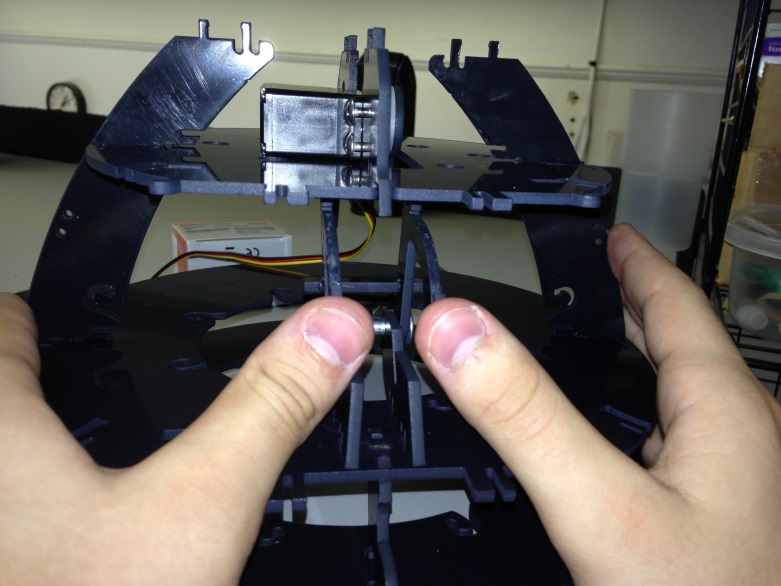
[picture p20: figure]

Attach Front Plate (top part first) to holes in part F.

Push plate back until it clicks into place in bottom.

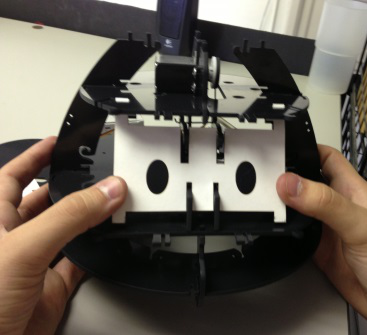
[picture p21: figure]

Pull eyelid mechanism forward and place eyelids

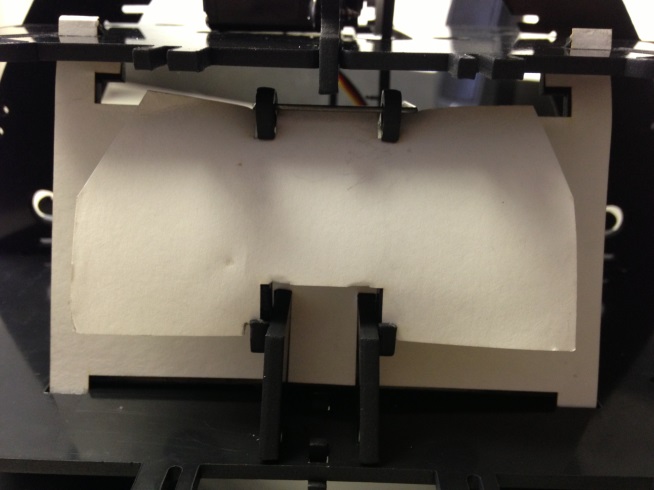
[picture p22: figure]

Attach Parts N to either side of robot.

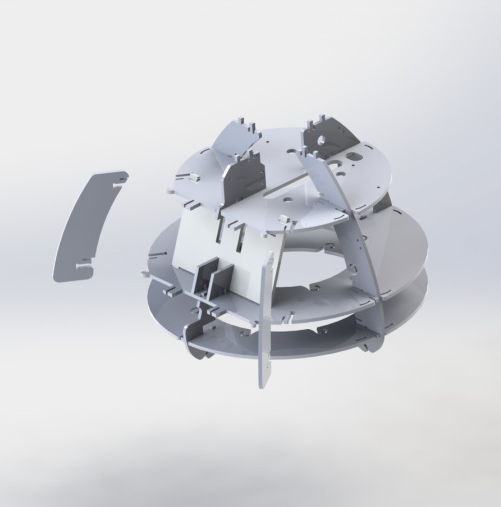
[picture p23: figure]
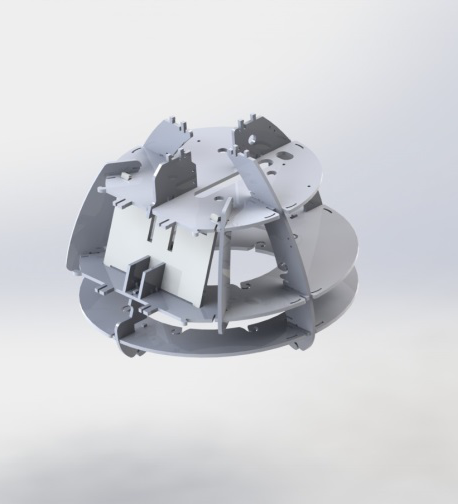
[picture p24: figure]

Attach Eye Plates (flat one (i) first). (your Eye Plate ii may be clear)

Screw in Satellite Board with fiber optic cables to the back of the robot.

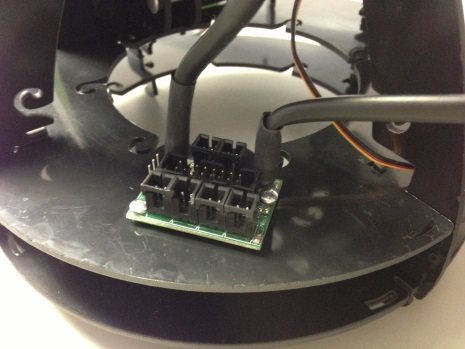
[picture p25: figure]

Looking at robot from behind, grab the left-most fiber optic cable and feed it through back most circle hole.

Then feed the same cable down through the next hole up.

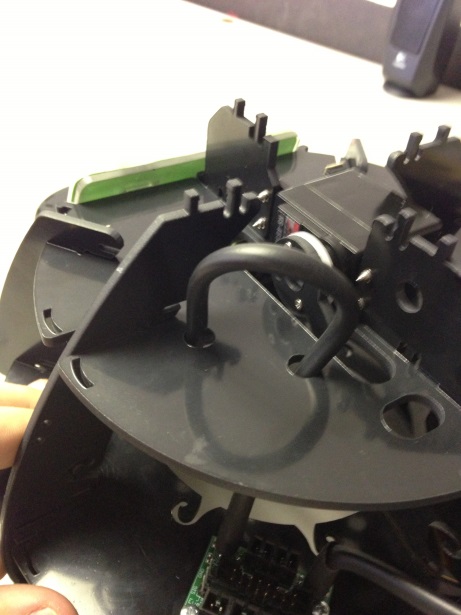
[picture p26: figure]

Feed cable up through the next hole up.

Repeat process with right most fiber optic cable, mirroring holes used by the left one

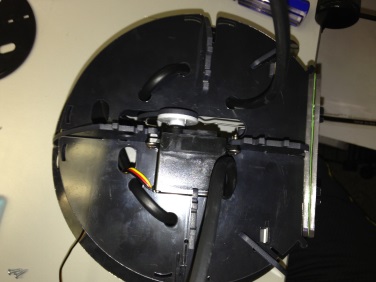
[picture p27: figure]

Attach Final Plate (Part O) Be sure to feed Fiber Optic Cables through the holes.

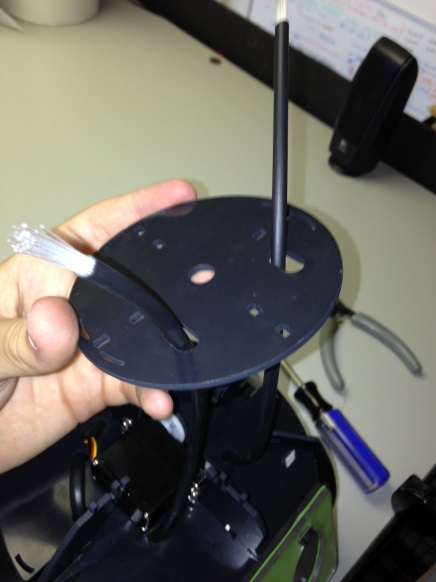
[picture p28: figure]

Attach Wi-Fly board and screw in (s3).

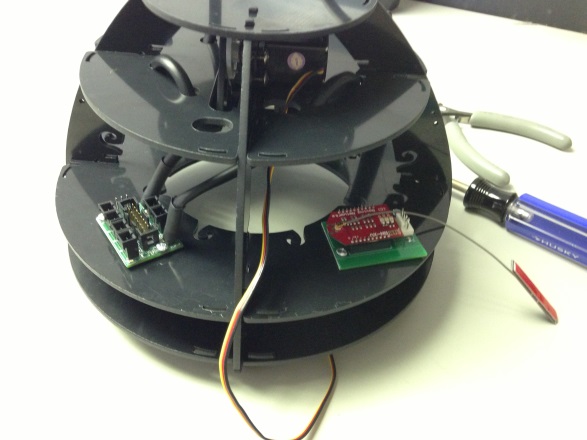
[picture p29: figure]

Screw in Touch Switches (s4).

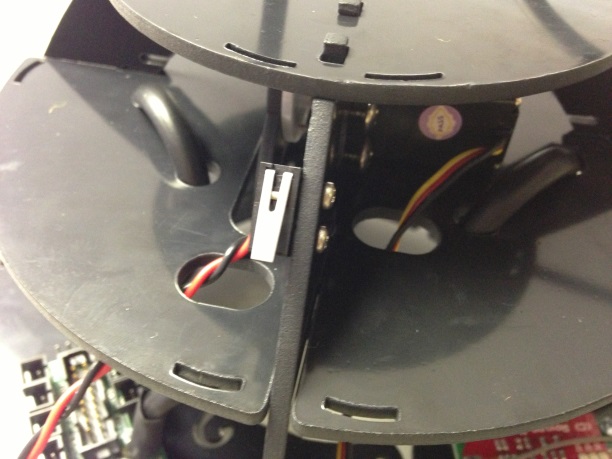
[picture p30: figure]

Part 2: Base Construction

Materials Needed:

- Plastic Romibo Parts (16)
- Hot Glue Gun
- Screwdriver
- Screws (# varies) (14 for R3 model)
- Speaker
- Infared Sensor
- Battery Pack with on/off switch
- Arduino Board with Romibo Shield

Steps

Build Neck by sliding B1 and B2 into A1 and A2

Slide A2 on to close.

***solid works files****

Slide neck assembly into top plate C

Add Servo Arms to Servos, then attach to B2 ensuring that servo arms are curved inward.

***dropbox photo****

Screw Servos into B1

Put motors through holes in plates D1 and D2. Ensure that they mirror each other.

***dropbox photo****

Connect D1 and D2 to C

***dropbox photo****

Hot-glue Speaker to Front Plate E. It is important that the speakers go on the side that the servos are not on. It will not fit otherwise

***dropbox photo***

Screw infrared sensor to opposite side of speaker on front plate. Feed the infrared cable through the hole in the plate.

***dropbox photo***

Attach front plate to the rest of the base

***dropbox photo and/or Solid Works***

Feed large and small rainbow ribbons through neck hole.

***dropbox photo***

Pass photo resistors through holes in front plate. Feed cable through hole made between plates D and C.

***dropbox photo***

On the D plate with holes in the side, attach smaller plates F1 and F2.

***dropbox photo***

Place Battery pack in gap and feed battery pack wires through same opening as photoresistor

***dropbox photo***

Attach outer plate G (the one with holes) to F1, F2, and C.

***dropbox photo***

Attach Battery pack on/off switch to back plate

Attach everything to the Arduino Shield. Ensure that the servo black cable is in line with the Gnd cable.

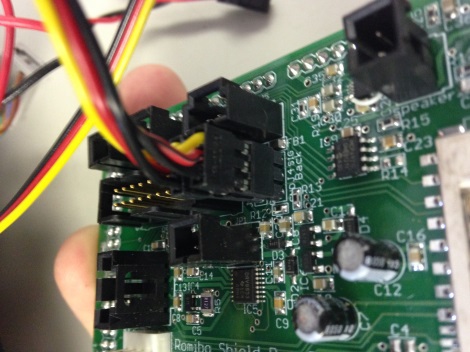
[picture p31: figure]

***dropbox photo + diagram***

Mount the Arduino Board to D plate and screw in.

***photo***

Attach part H

***photo***

Mount Bottom Plate * onto bottom of base.

***photo***

Slide locking plates J1 and J2 over knobs and then slide towards center.

***photo***

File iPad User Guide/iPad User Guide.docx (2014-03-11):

# iPad User Guide

# Connecting the iPad to the Romibo

First, turn on the robot by toggling the On/Off switch on the back of the robot to the On position

Next turn on the iPad by pressing the power button on the upper right edge.

## step 1: Connecting with Settings

Tap the Settings button

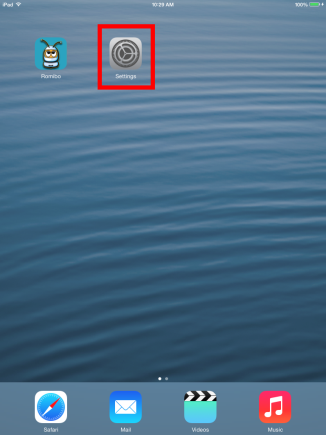
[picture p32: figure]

Along the left column, tap the line that says WiFi

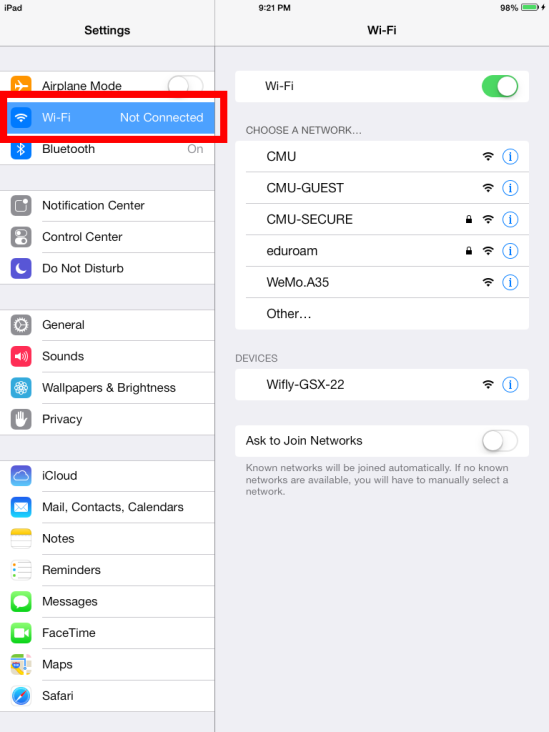
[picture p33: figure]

On the right column, look for the “Devices” heading. Underneath it will be a line that says “Wifly-GSX-22” – this is the robot’s network. If you don’t see the “Devices” heading or the Wifly line, try changing the robot’s batteries and turning it on again. If that doesn’t help, contact one of the developers.

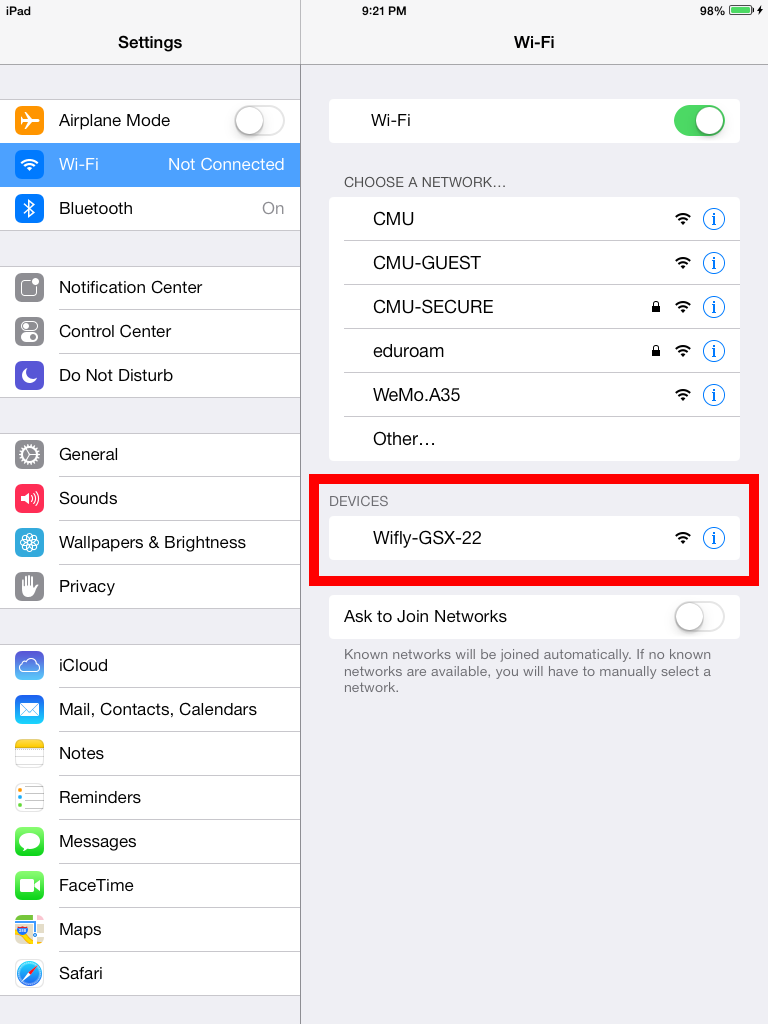
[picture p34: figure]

Tap the text “Wifly-GSX-22.” It will pop up a message to let you know that the network isn’t connected to the internet – click “Join Anyway”

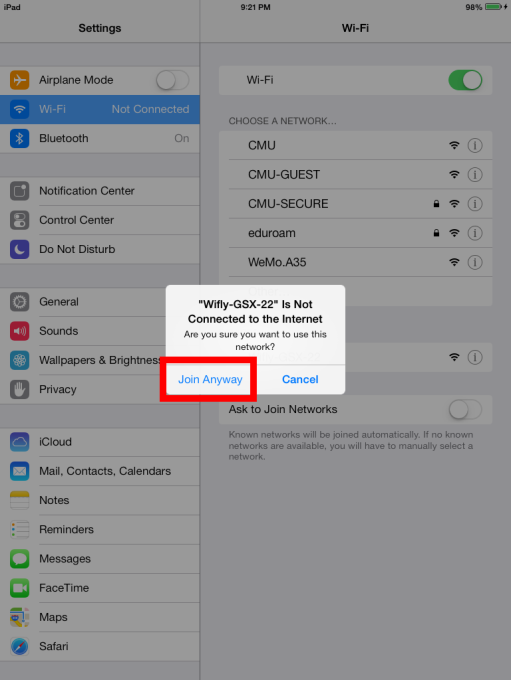
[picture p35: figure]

The Wifly line will jump to the top of the screen and get a blue checkmark.

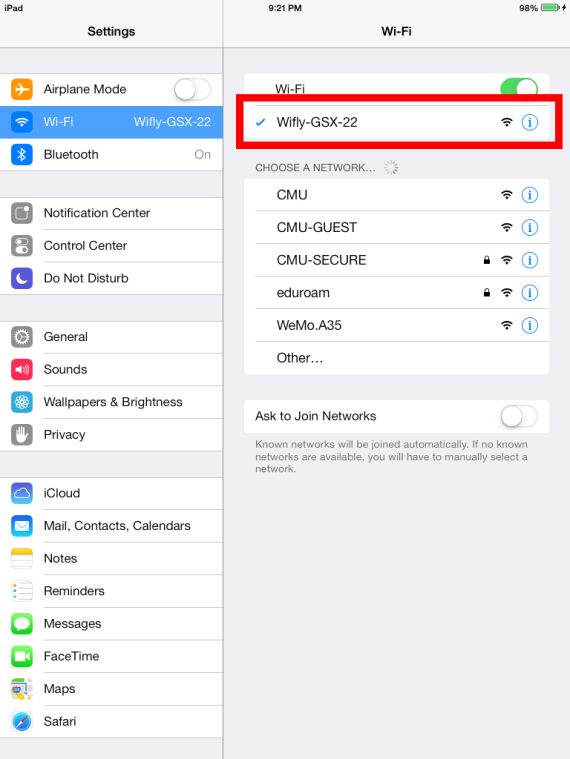
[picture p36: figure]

Tap the “Wifly-GSX-22” text again to see the connection details. The IP Address and Subnet Mask boxes will be empty – the iPad and the robot have to talk to each other for a minute to figure out what goes here.

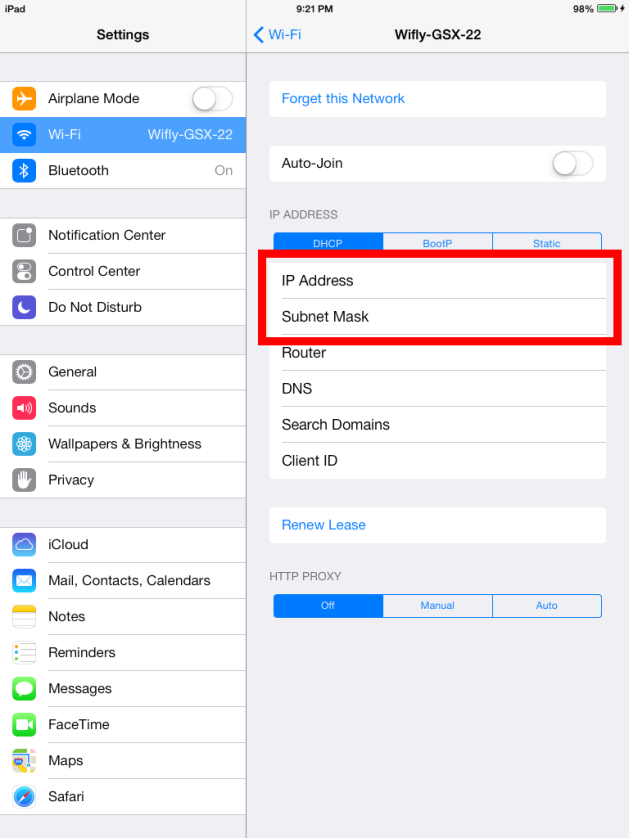
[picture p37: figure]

To see if the connection has been made, you have to refresh this details screen. To refresh, click the blue Wi-Fi arrow at the top of the right column.

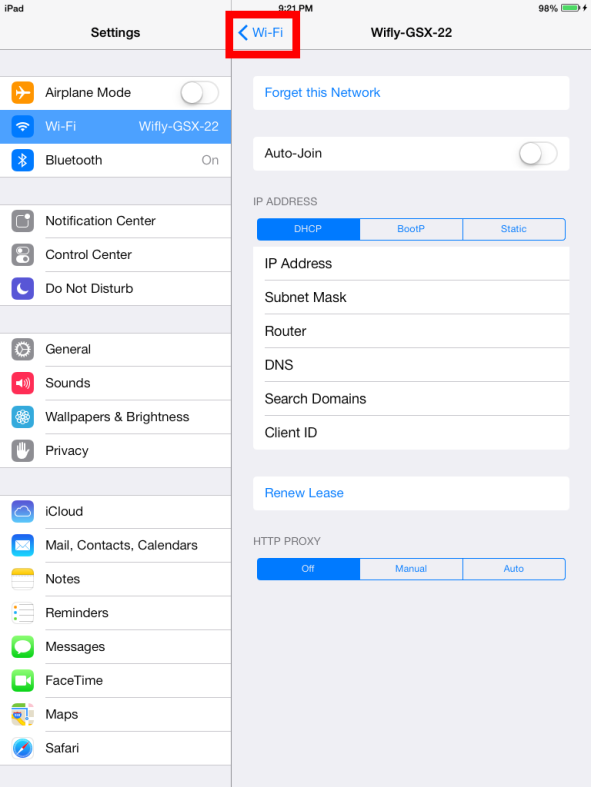
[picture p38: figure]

This takes you back to the list of networks we saw earlier. Click the “Wifly-GSX-22” line to view the details screen again.

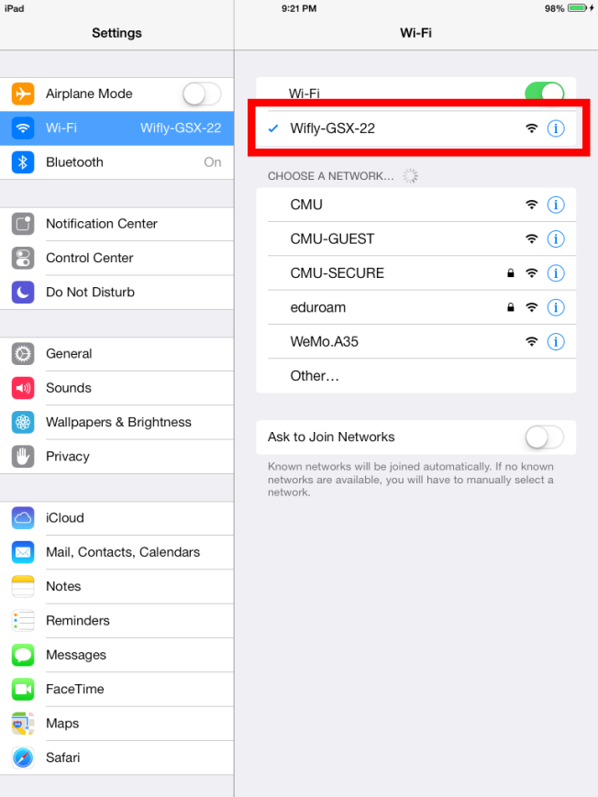
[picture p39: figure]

You might have to go back and forth between the details page and the list of networks a few times before the robot and the iPad are connected. When everything’s ready to go, the IP Address and Subnet Mask boxes will have numbers in them. (Don’t worry about what the exact numbers are, just make sure the boxes aren’t empty.)

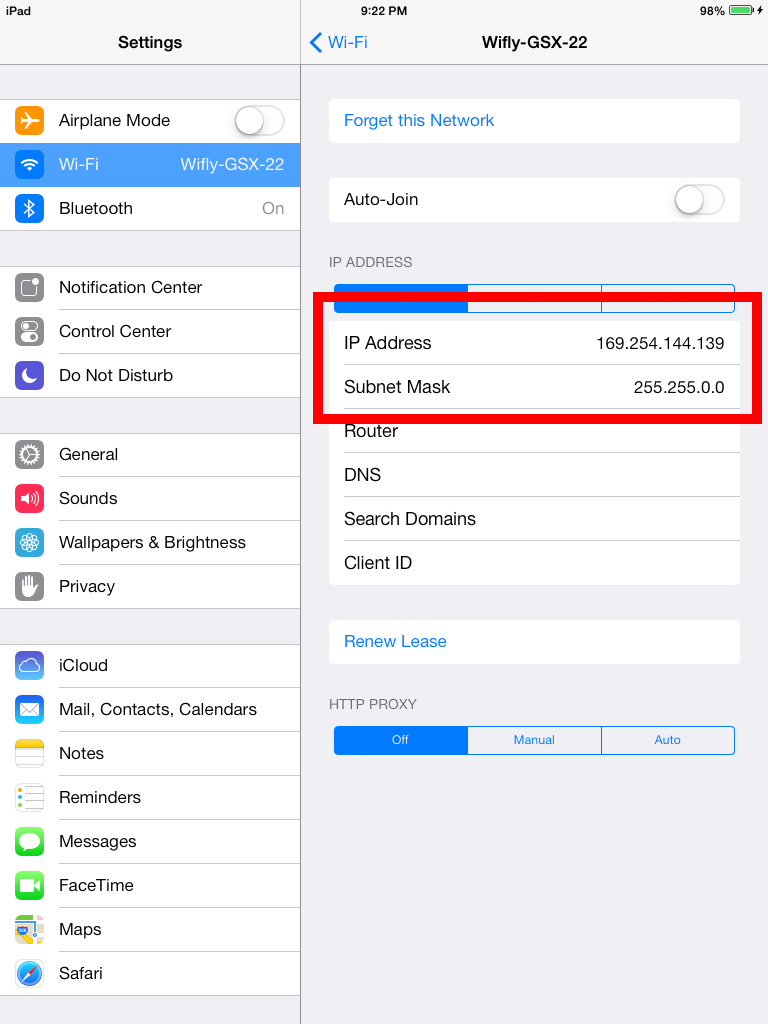
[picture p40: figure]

To close Settings, press the Home button at the bottom of the iPad – it’s the physical button shaped like a circle with a picture of a rounded square in the center.

## step 2: Connecting with the Romibo App

Tap the Romibo application button.

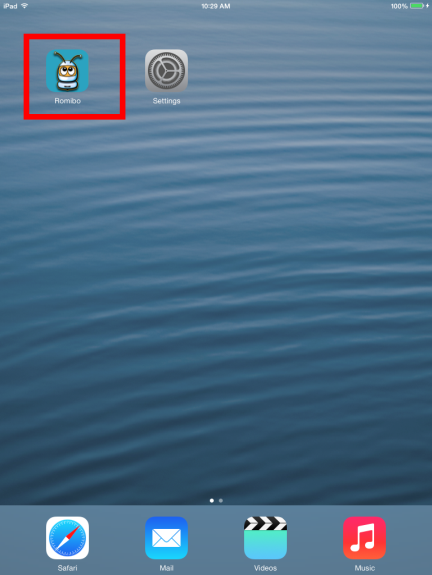
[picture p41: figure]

In the upper left, tap the Gear button to open the Romibo connection buttons. Notice how next to the gear button it says “Not connected”

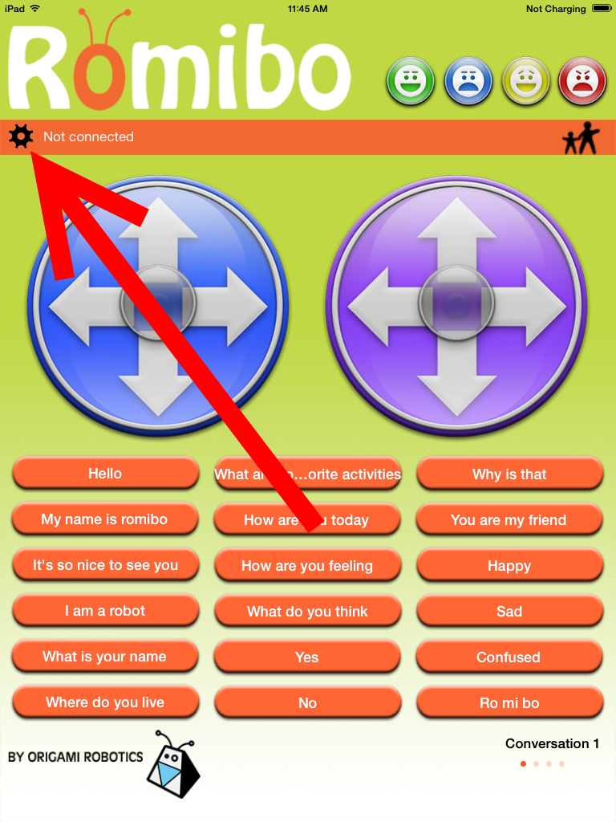
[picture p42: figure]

Tap the “Connect to Romibo” text.

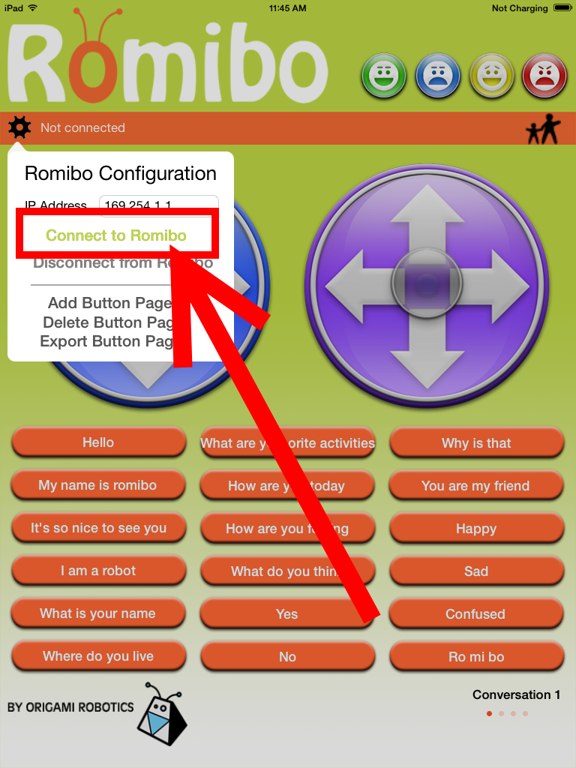
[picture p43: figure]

The dialog box will disappear and the text next to the gear button will say “Connected”

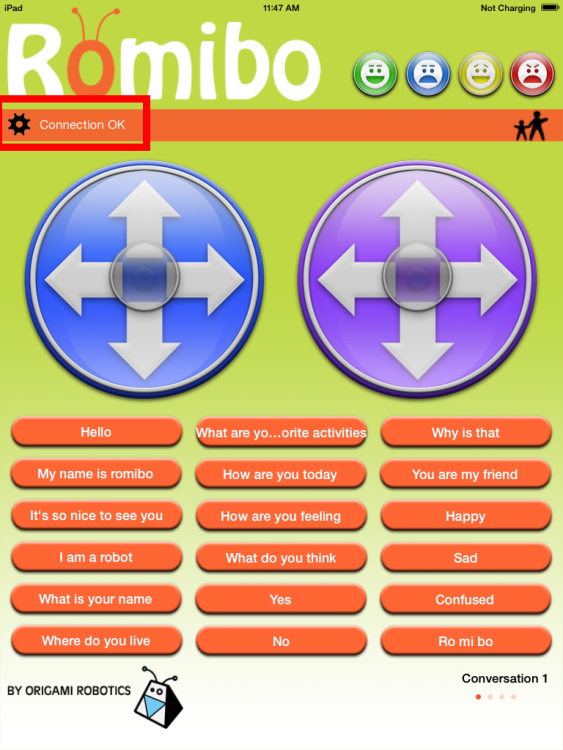
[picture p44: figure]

Now the robot is connected and ready to control.

# Troubleshooting

## The robot says connected but isn’t responding to the ipad

First, follow the instructions in Connecting with Settings (page 1) to make sure the details page for the WiFly-GSX-22 network has numbers in the IP Address and Subnet Mask boxes.

If that doesn’t help, disconnect and reconnect the Romibo. To do this, first tap the gear button in the upper left.

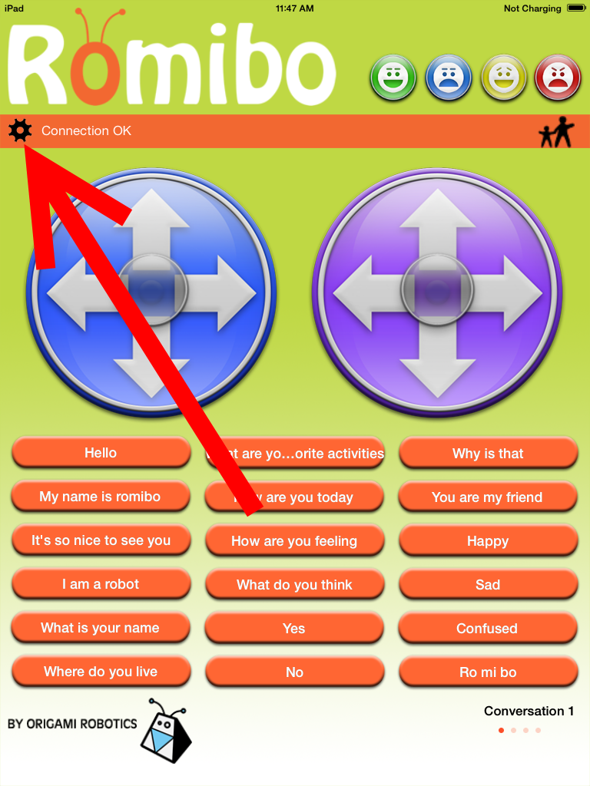
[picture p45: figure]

Next tap “Disconnect from Romibo”

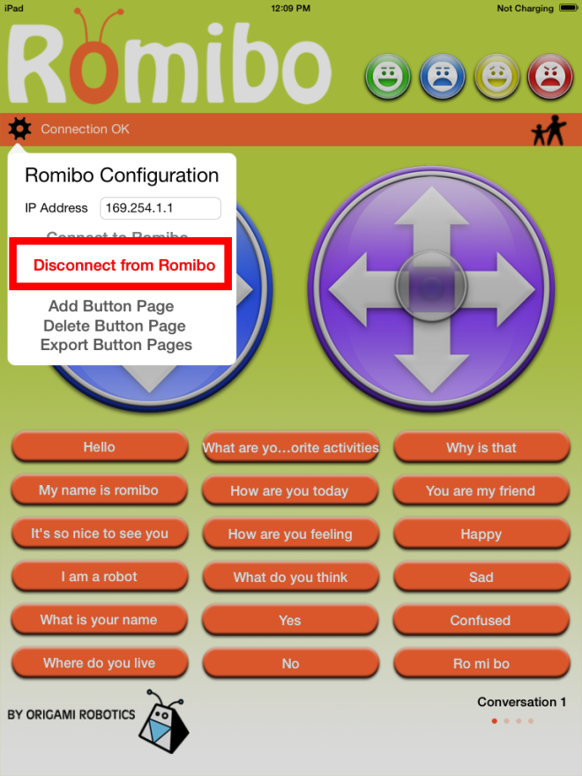
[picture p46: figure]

The dialog box will disappear the text “Not Connected” will be next to the gear button. Now click the gear button again.

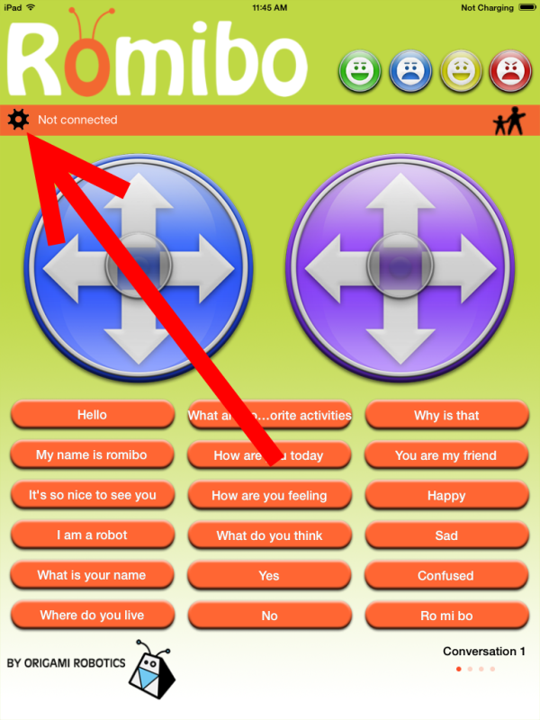
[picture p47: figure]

Tap the “Connect to Romibo” text.


The dialog box will disappear and the text next to the gear button will say “Connected”

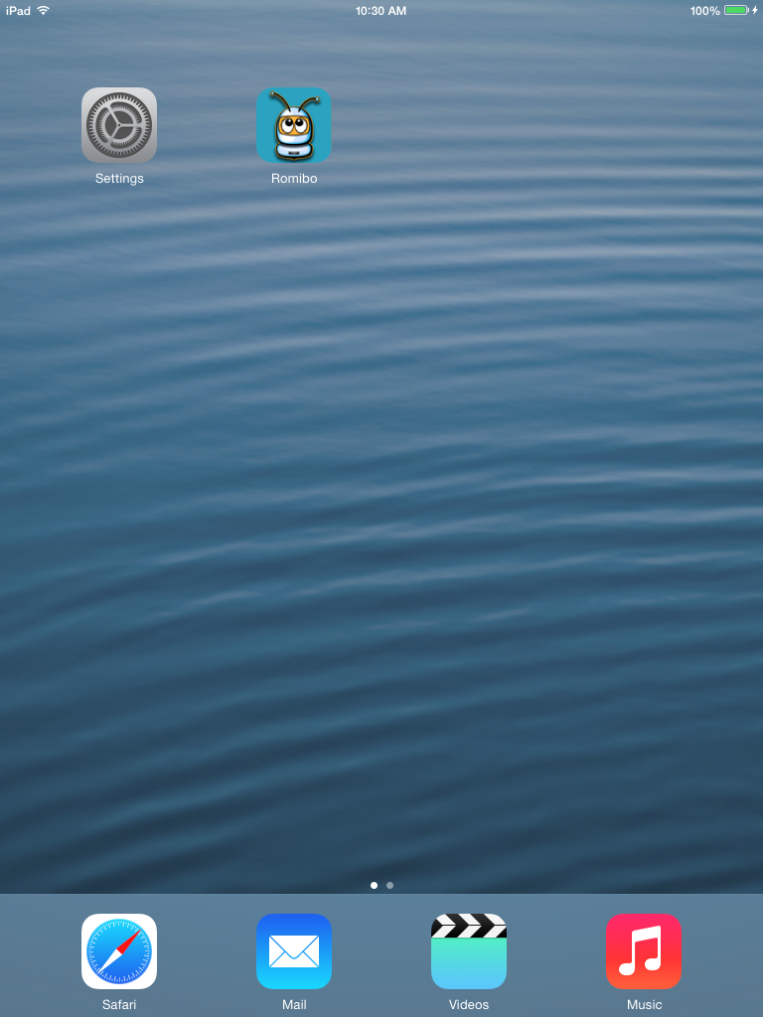
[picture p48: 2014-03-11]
iPad User Guide/Images/IMG_0008.PNG

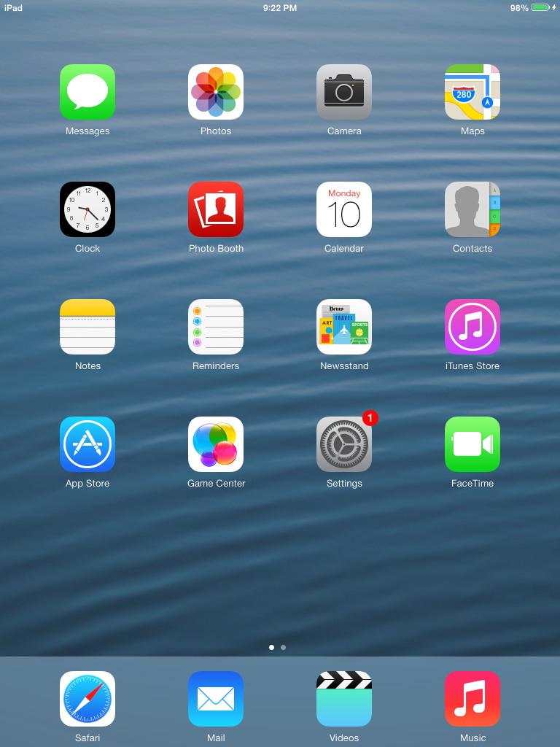
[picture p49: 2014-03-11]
iPad User Guide/Images/IMG_0006.PNG

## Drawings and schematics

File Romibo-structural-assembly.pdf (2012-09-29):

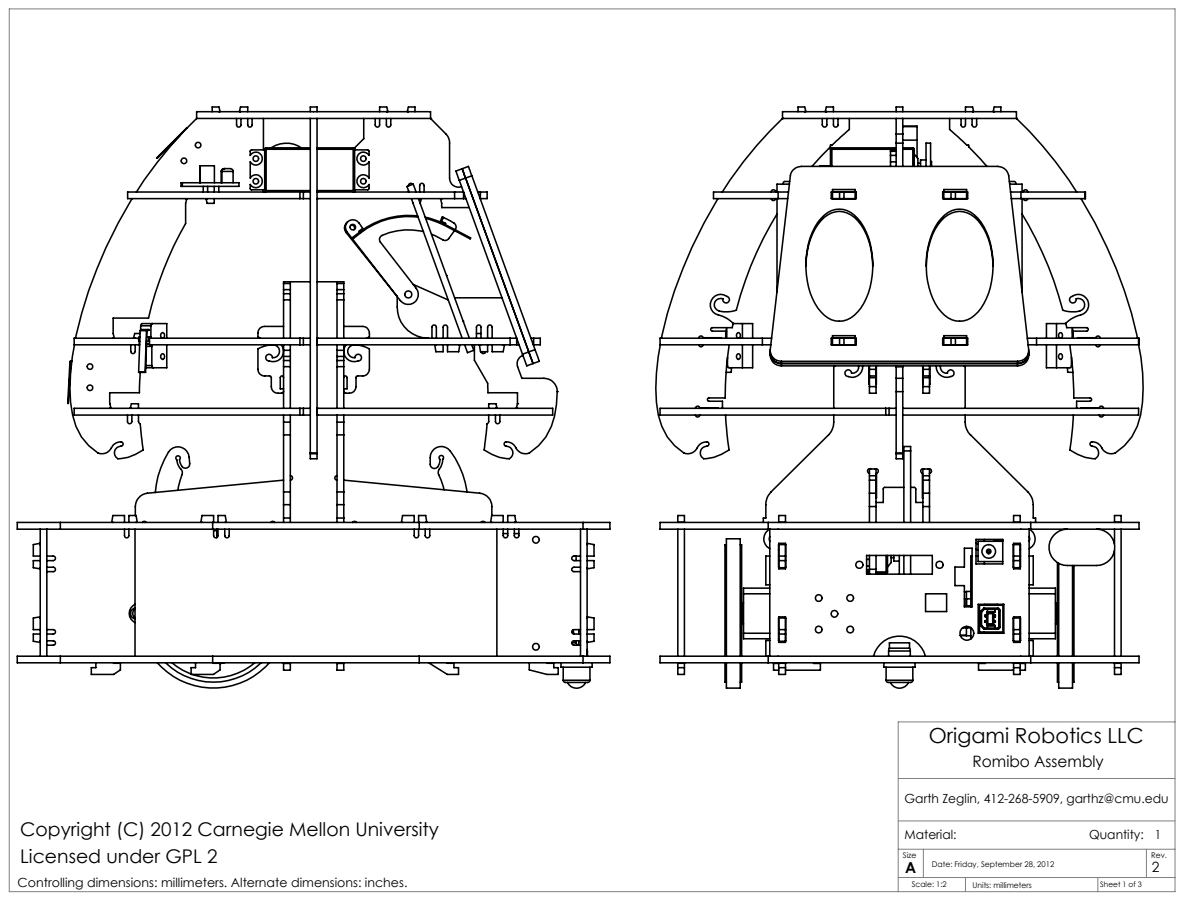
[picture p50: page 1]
Controlling dimensions: millimeters. Alternate dimensions: inches.; Units: millimeters

Origami Robotics LLC
Romibo Assembly

Garth Zeglin, 412-268-5909, garthz@cmu.edu2

Copyright (C) 2012 Carnegie Mellon University
Licensed under GPL 2

Size A Rev. | Date: Friday, September 28, 2012

Scale: 1:2 | | Sheet 1 of 3

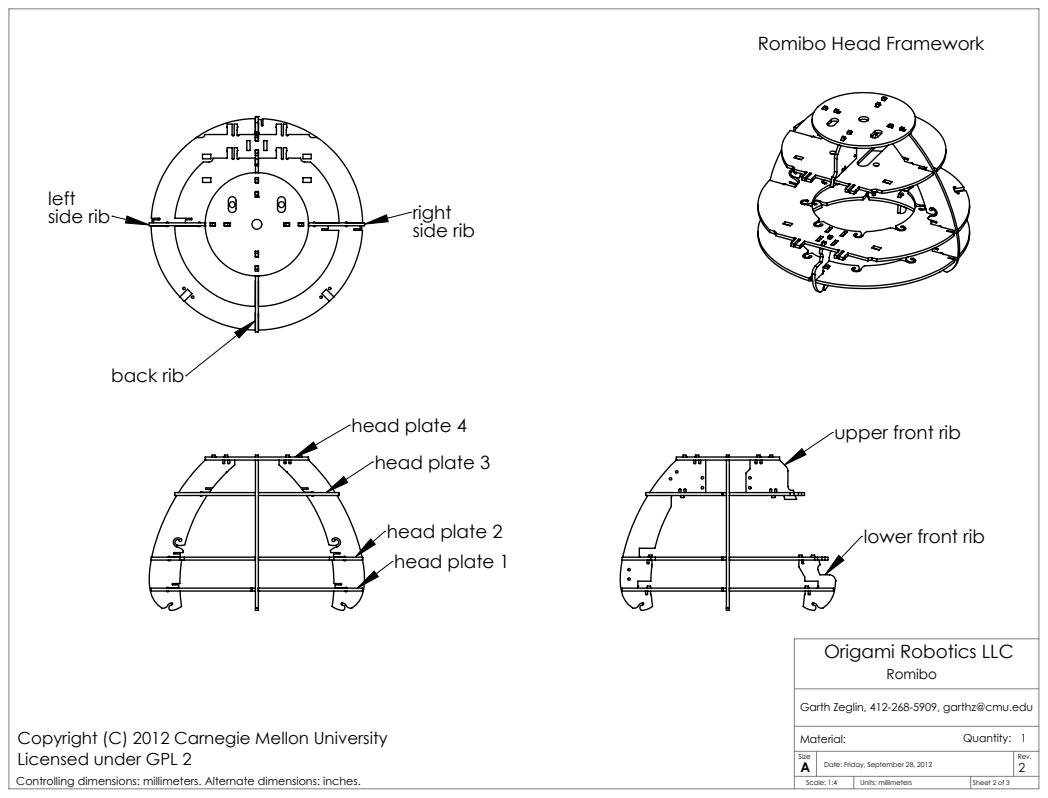
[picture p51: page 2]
head plate 1; head plate 2; head plate 3; head plate 4; side rib; back rib; Date: Friday, September 28, 2012 A; Rev.; Material:; Quantity: 1

Romibo Head Framework

upper front rib

lower front rib

Origami Robotics LLC

Garth Zeglin, 412-268-5909, garthz@cmu.edu

Copyright (C) 2012 Carnegie Mellon University
Licensed under GPL 2

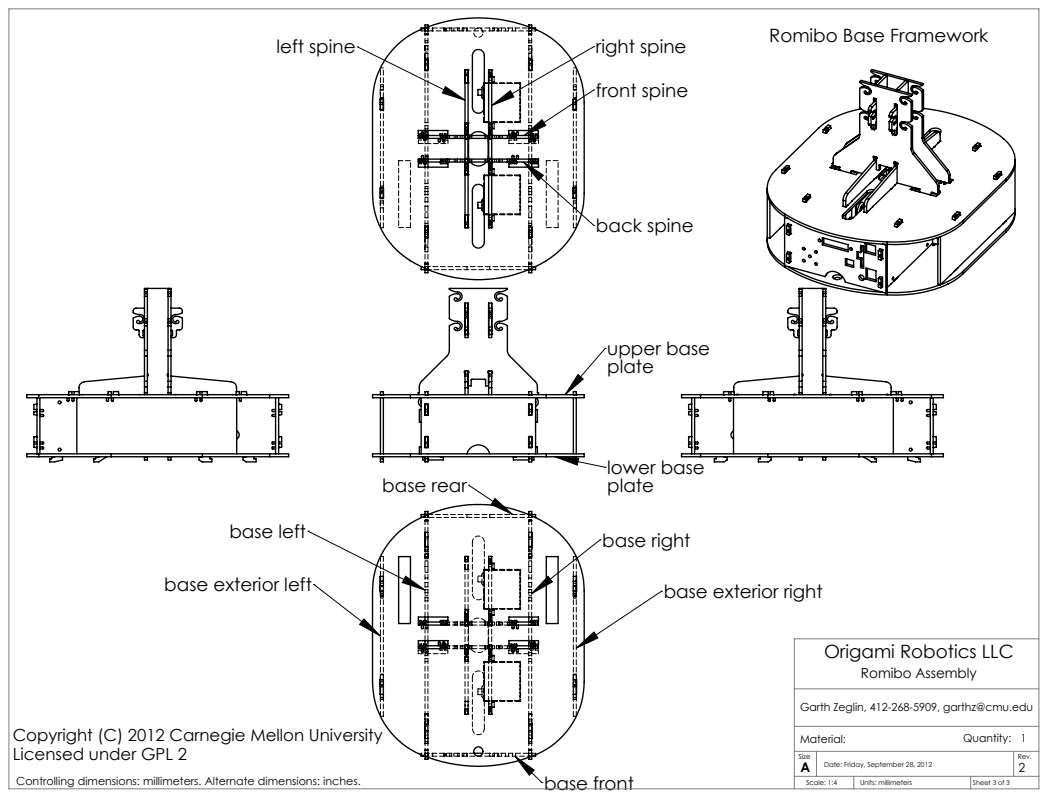
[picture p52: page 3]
upper base; lower base; left spine; right spine; front spine; back spine; base rear; base front; Date: Friday, September 28, 2012 A; Rev.; Material:; Quantity: 1

Romibo Base Framework

base right base left

base exterior right base exterior left

Origami Robotics LLC
Romibo Assembly

Garth Zeglin, 412-268-5909, garthz@cmu.edu

Copyright (C) 2012 Carnegie Mellon University
Licensed under GPL 2

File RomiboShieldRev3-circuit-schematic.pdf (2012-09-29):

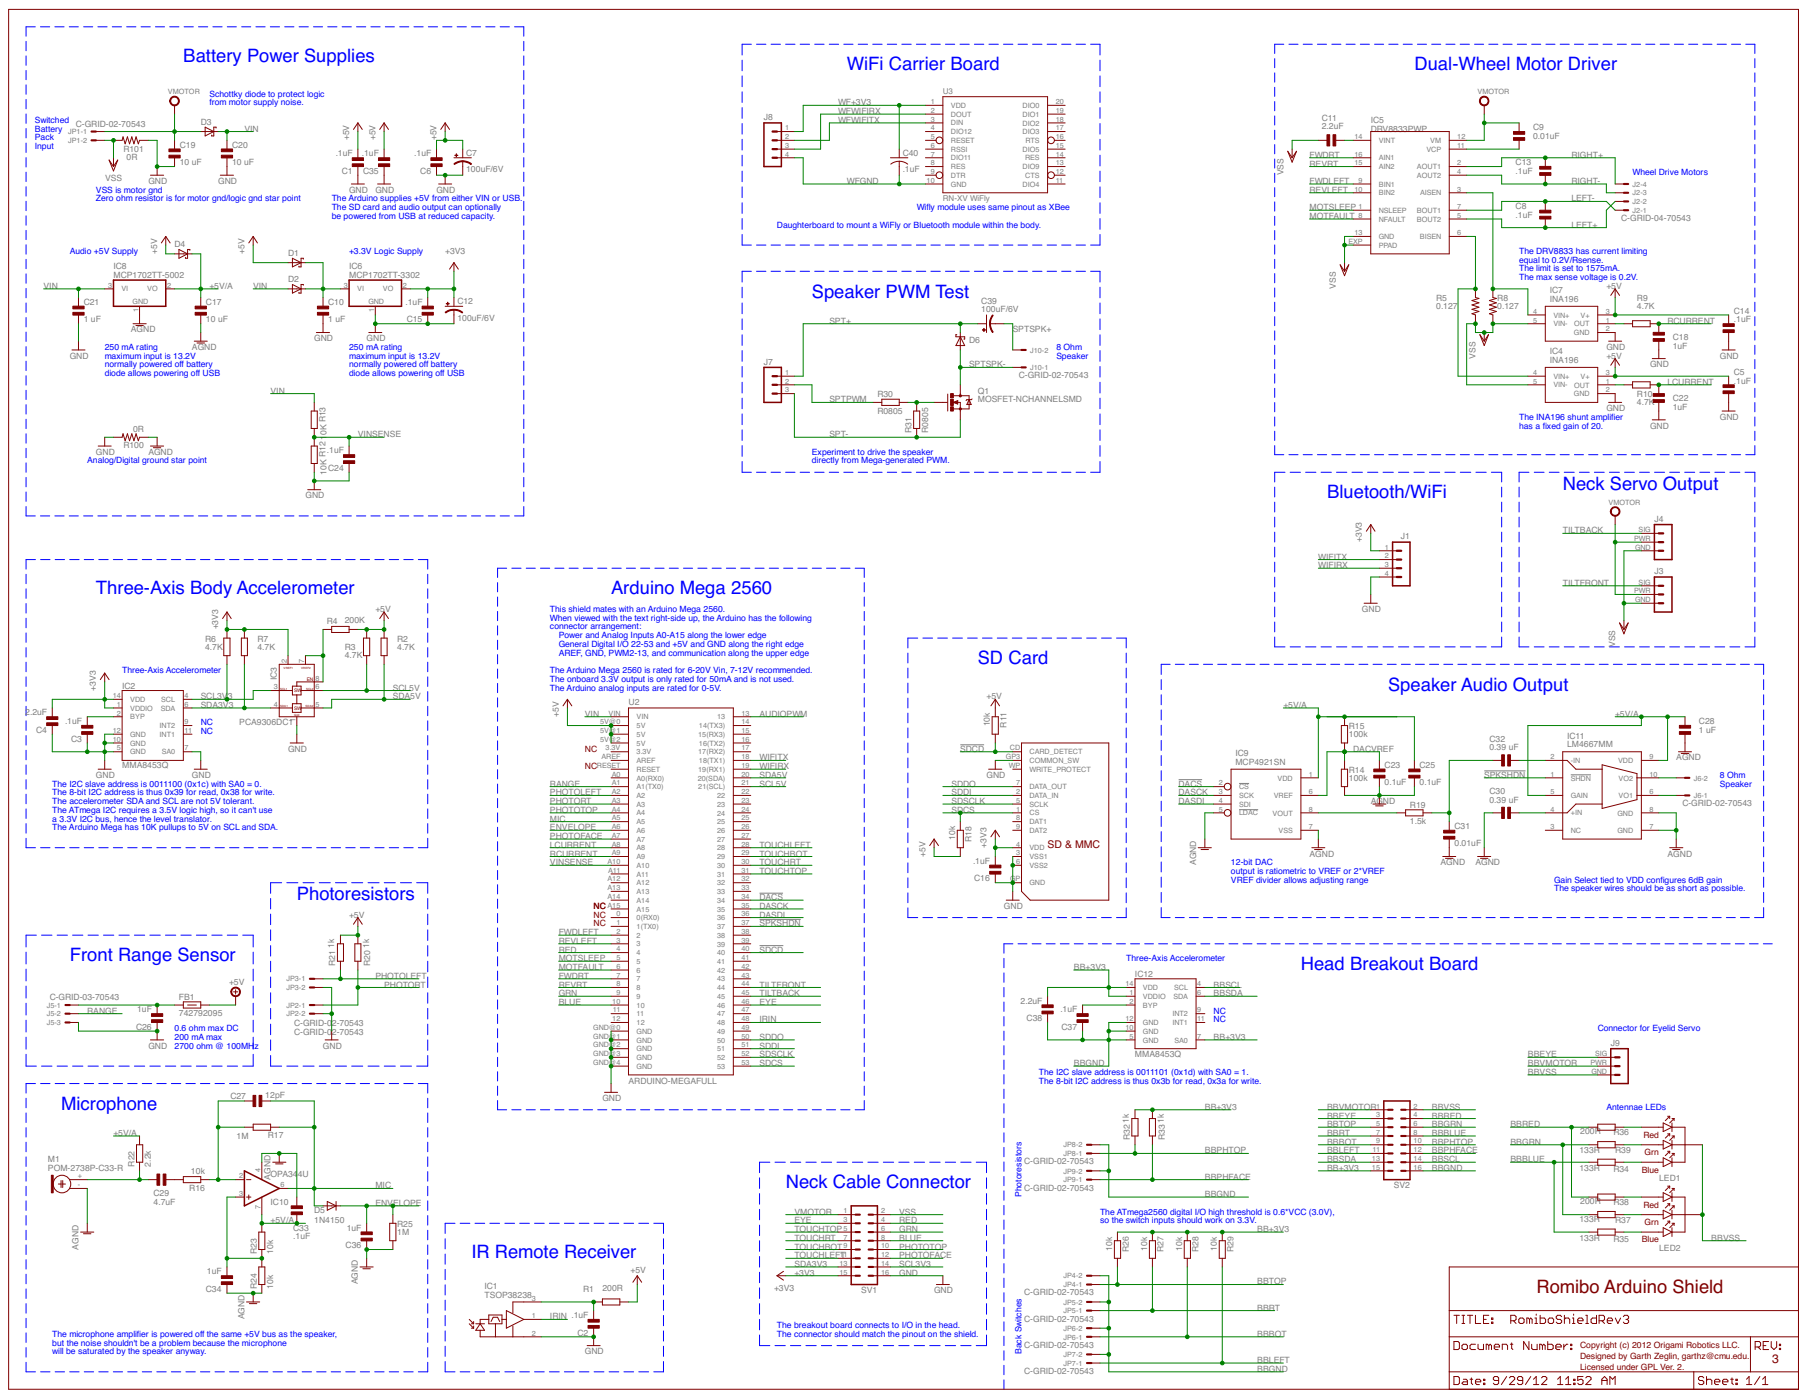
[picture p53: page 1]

Dual-Wheel Motor Driver

from motor supply noise.

LEFT- LEFT+ RIGHT- RIGHT+

VSS
VSS is motor gnd Zero ohm resistor is for motor gnd/logic gnd star point

RN-XV WiFly
Wifly module uses same pinout as XBee

The SD card and audio output can optionally be powered from USB at reduced capacity.

Daughterboard to mount a WiFly or Bluetooth module within the body.

The DRV8833 has current limiting
equal to 0.2V/Rsense. The limit is set to 1575mA. The max sense voltage is 0.2V.

250 mA rating maximum input is 13.2V

The INA196 shunt amplifier has a fixed gain of 20.

Analog/Digital ground star point

Experiment to drive the speaker directly from Mega-generated PWM.

Three-Axis Body Accelerometer

This shield mates with an Arduino Mega 2560. When viewed with the text right-side up, the Arduino has the following Power and Analog Inputs A0-A15 along the lower edge General Digital I/O 22-53 and +5V and GND along the right edge AREF, GND, PWM2-13, and communication along the upper edge

The Arduino Mega 2560 is rated for 6-20V Vin, 7-12V recommended. The onboard 3.3V output is only rated for 50mA and is not used. The Arduino analog inputs are rated for 0-5V.

The accelerometer SDA and SCL are not 5V tolerant. The I2C slave address is 0011100 (0x1c) with SA0 = 0.
The 8-bit I2C address is thus 0x39 for read, 0x38 for write. The Arduino Mega has 10K pullups to 5V on SCL and SDA. The ATmega I2C requires a 3.5V logic high, so it can't use a 3.3V I2C bus, hence the level translator.

Gain Select tied to VDD configures 6dB gain The speaker wires should be as short as possible. 12-bit DAC
output is ratiometric to VREF or 2*VREF VREF divider allows adjusting range

The I2C slave address is 0011101 (0x1d) with SA0 = 1. The 8-bit I2C address is thus 0x3b for read, 0x3a for write.

The ATmega2560 digital I/O high threshold is 0.6*VCC (3.0V), so the switch inputs should work on 3.3V.

The microphone amplifier is powered off the same +5V bus as the speaker, but the noise shouldn't be a problem because the microphone will be saturated by the speaker anyway.

The breakout board connects to I/O in the head. The connector should match the pinout on the shield.

Copyright (c) 2012 Origami Robotics LLC. Designed by Garth Zeglin, garthz@cmu.edu. Licensed under GPL Ver. 2.

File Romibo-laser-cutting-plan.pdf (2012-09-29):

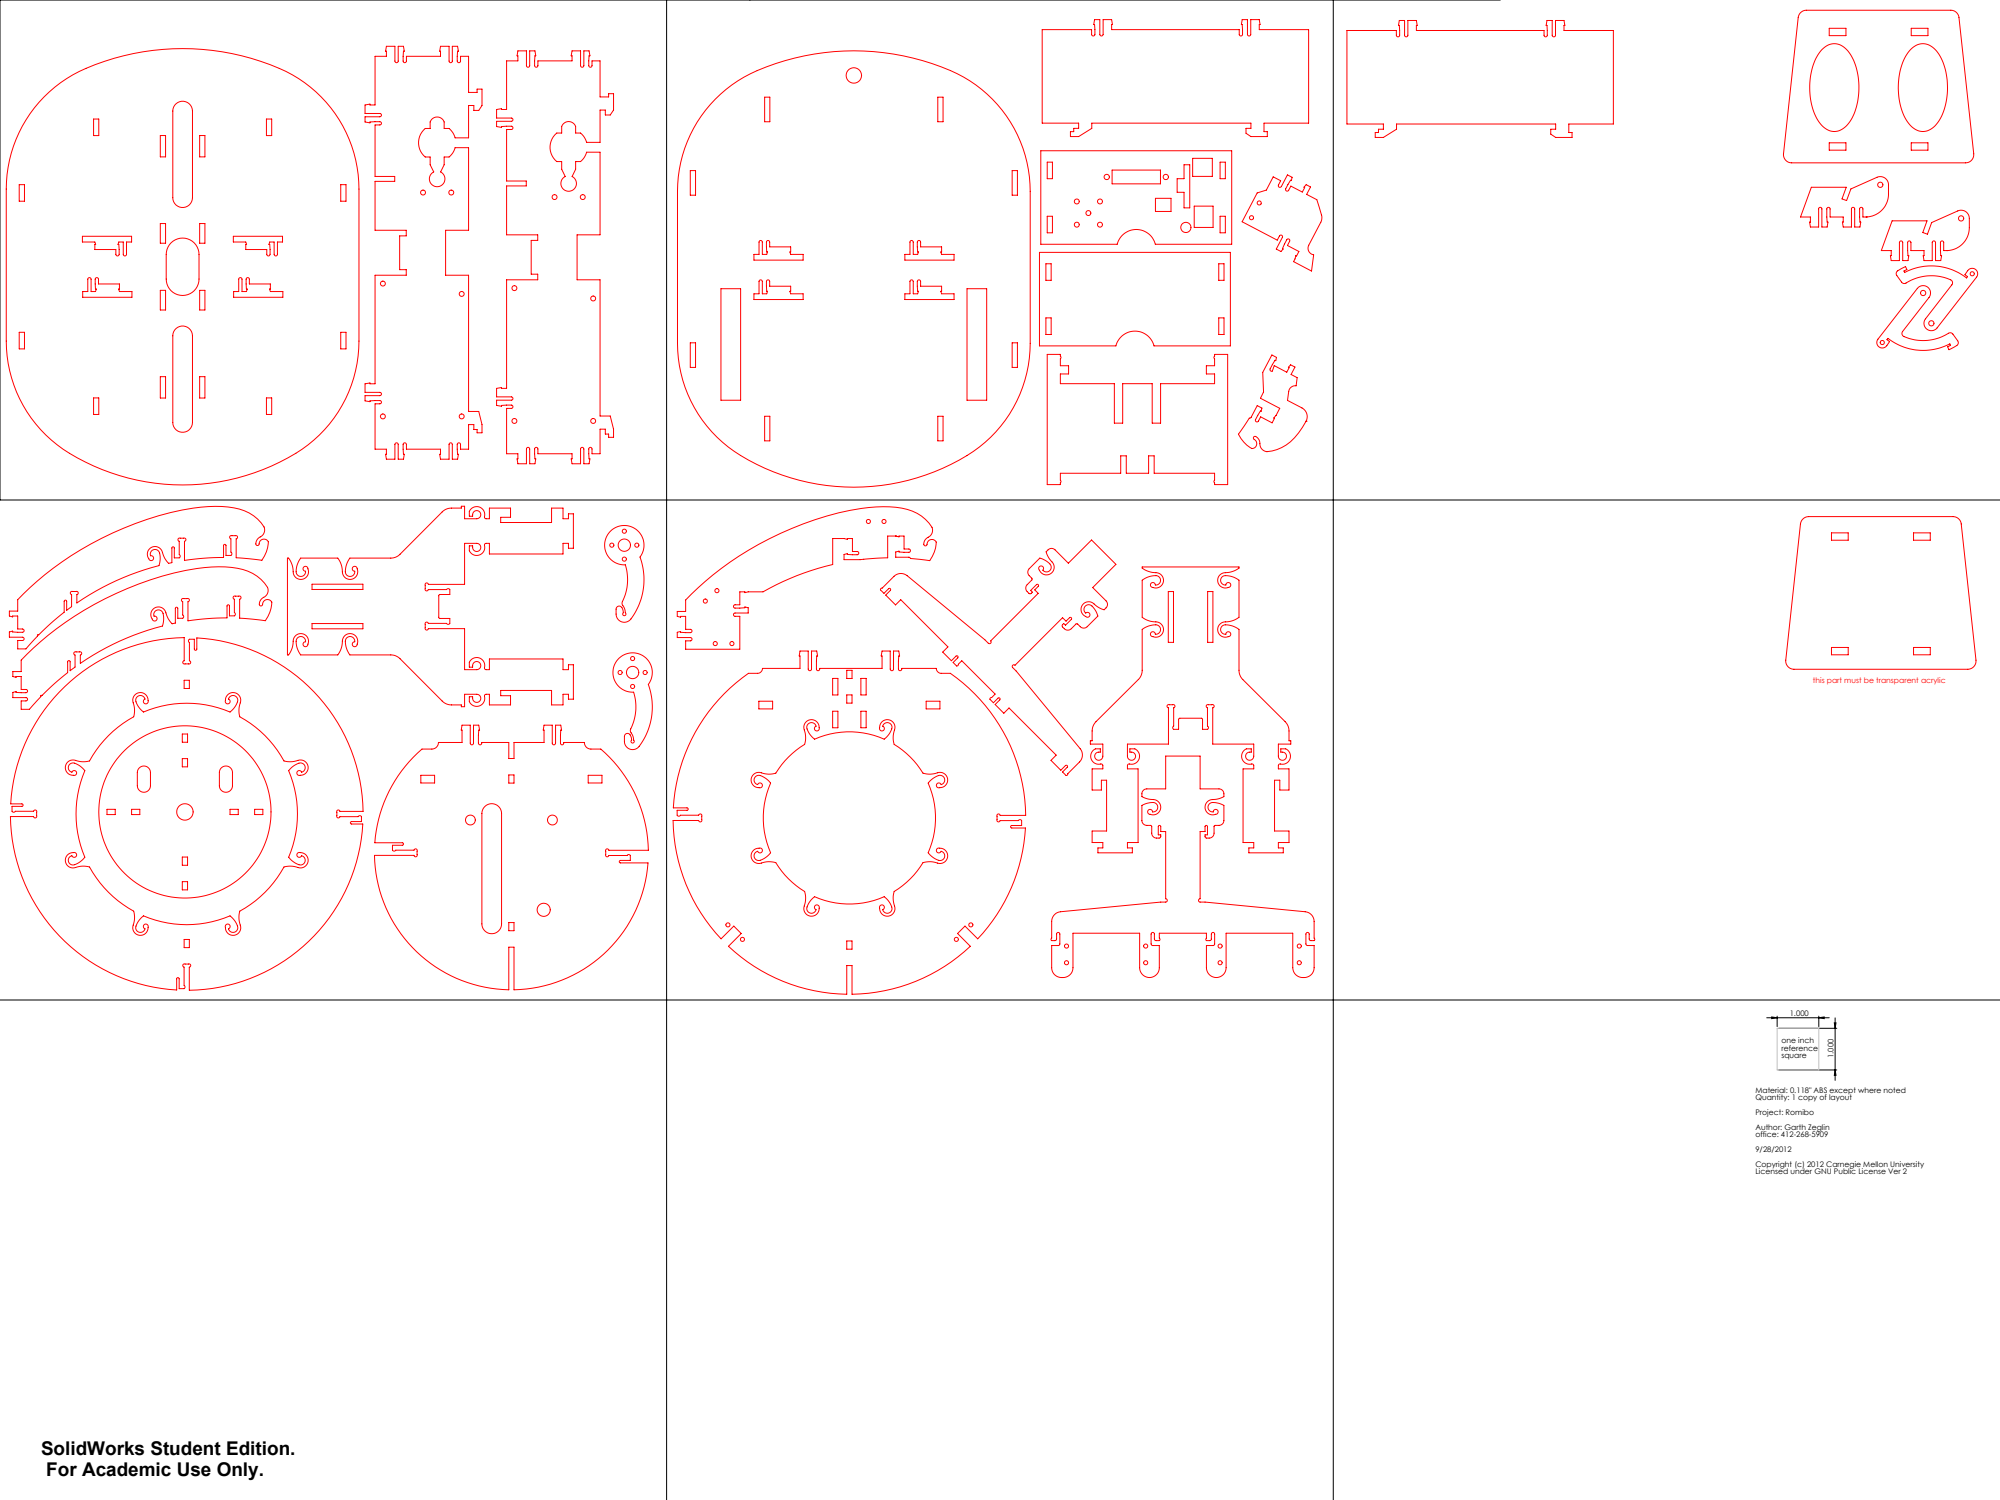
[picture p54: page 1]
one inch

this part must be transparent acrylic

Material: 0.118" ABS except where noted
Quantity: 1 copy of layout
Project: Romibo
Author: Garth Zeglin
office: 412-268-5909
Copyright (c) 2012 Carnegie Mellon University
Licensed under GNU Public License Ver 2

SolidWorks Student Edition.
For Academic Use Only.

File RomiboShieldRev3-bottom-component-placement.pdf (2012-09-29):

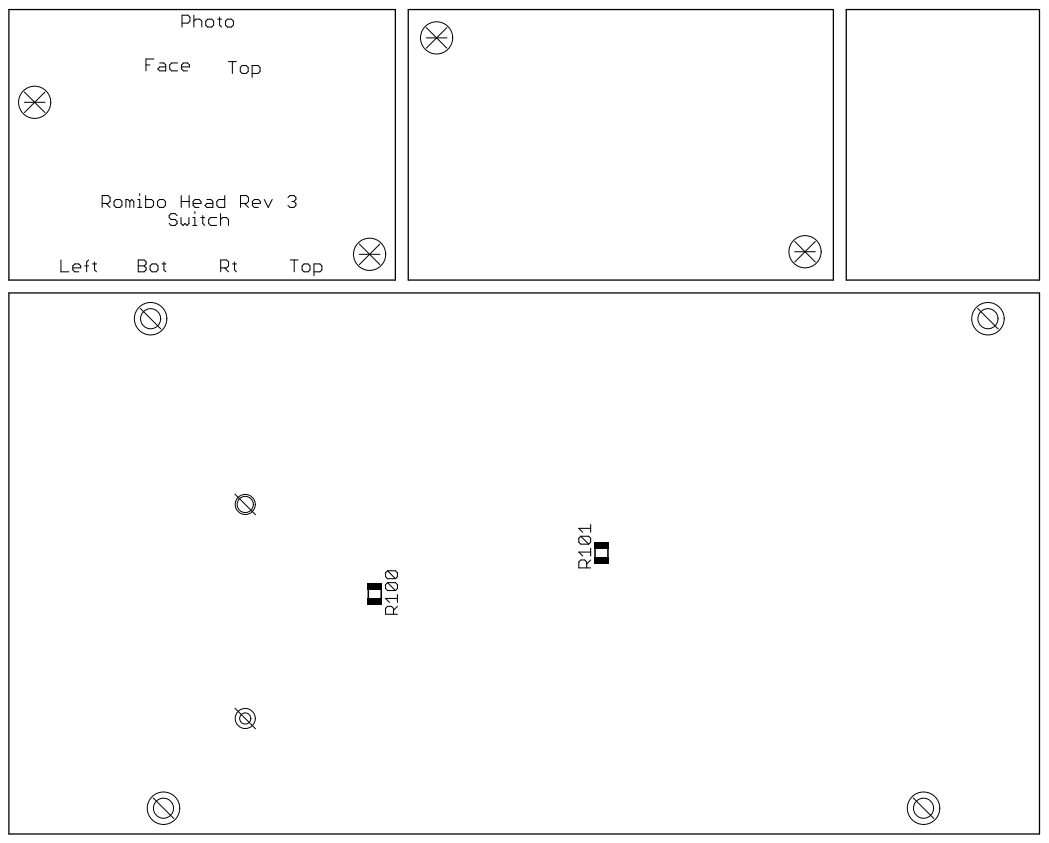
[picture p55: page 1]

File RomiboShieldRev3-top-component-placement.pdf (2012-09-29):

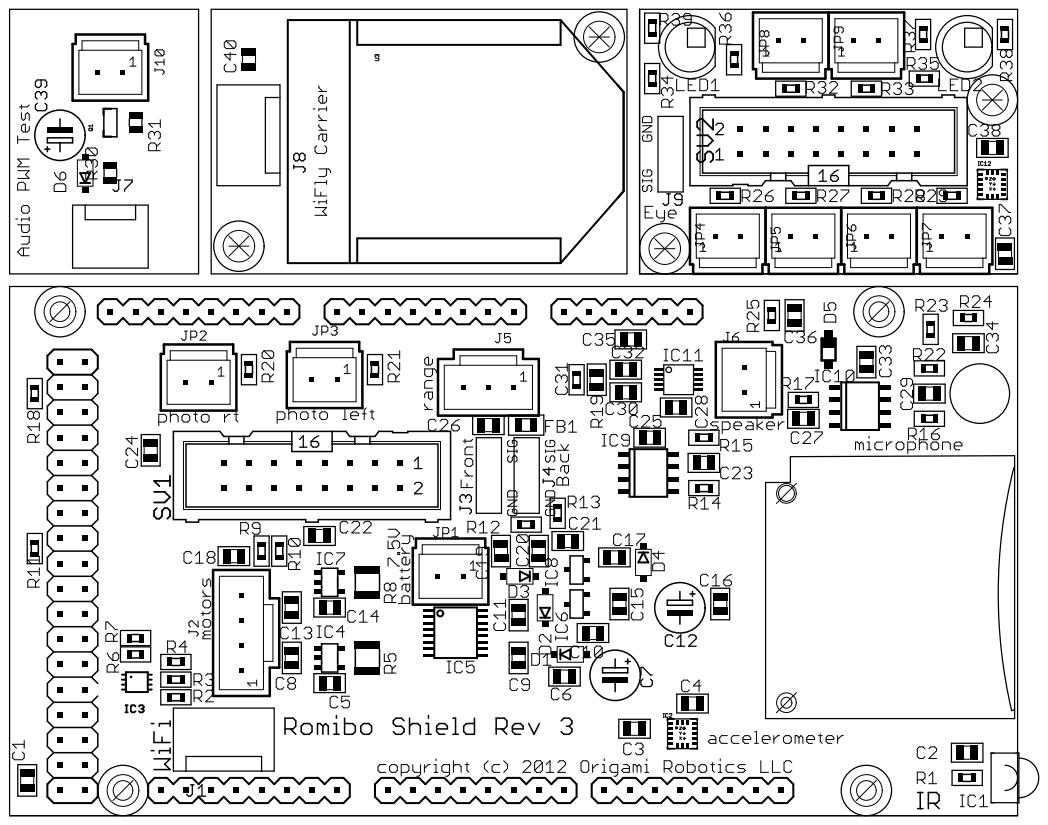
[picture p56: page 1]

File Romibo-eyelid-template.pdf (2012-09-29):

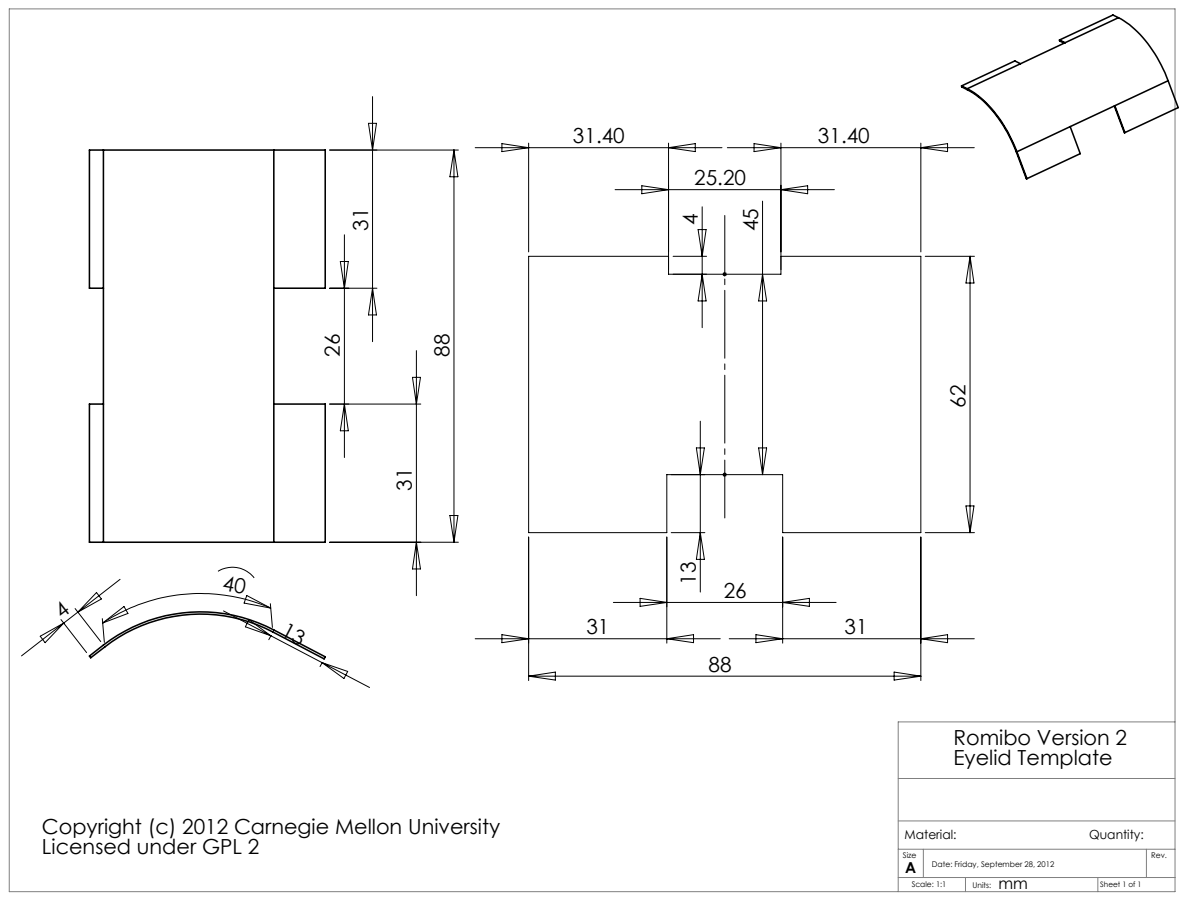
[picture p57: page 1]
Romibo Version 2 Eyelid Template

Copyright (c) 2012 Carnegie Mellon University
Licensed under GPL 2

Size | Date: Friday, September 28, 2012 A | Rev.
Scale: 1:1 | mm Units: | Sheet 1 of 1

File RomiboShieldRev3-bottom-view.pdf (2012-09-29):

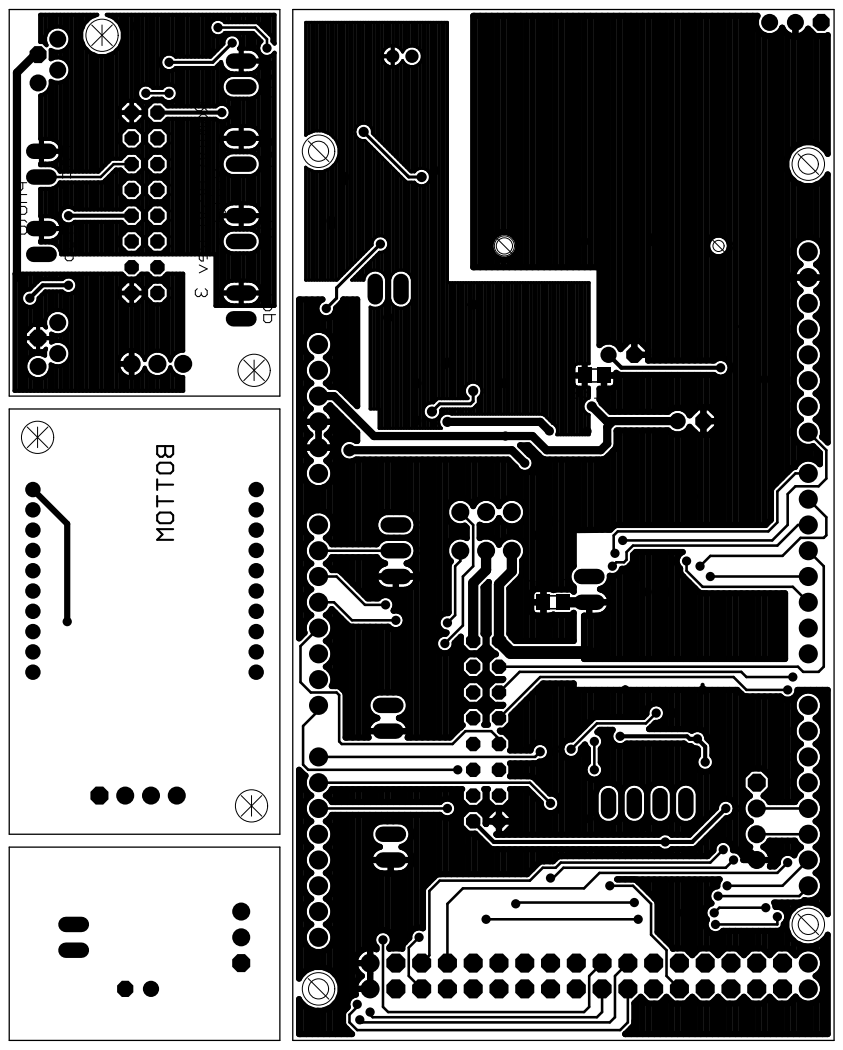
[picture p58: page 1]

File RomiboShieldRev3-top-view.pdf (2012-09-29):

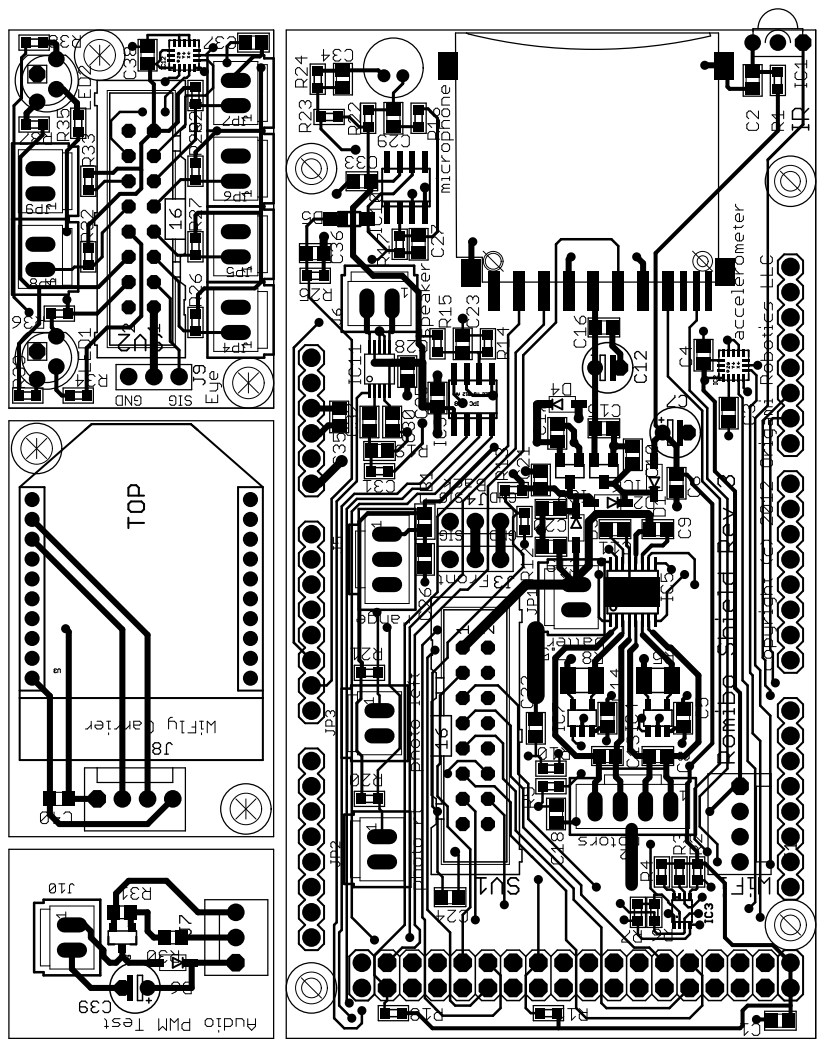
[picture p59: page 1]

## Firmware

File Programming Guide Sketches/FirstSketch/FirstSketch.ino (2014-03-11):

void setup()
{
  pinMode (2, OUTPUT);
  pinMode (5, OUTPUT);
  pinMode (6, OUTPUT);
  pinMode (7, OUTPUT);

  digitalWrite (5, HIGH);
  digitalWrite (6, HIGH);
}

void loop()
{

  digitalWrite (2, HIGH);
  digitalWrite (7, HIGH);
  delay(1000);
  
  digitalWrite (2, LOW);
  digitalWrite (7, LOW);
  delay(1000);
}

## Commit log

2012-09-29 Added license text, mechanical drawings, electronic drawings, and a HOWTO on Bluetooth.
    [Romibo-laser-cutting-plan.dxf]
2014-01-06 Updated Programming Manual
    Added program on loops, analog output, and LED lighting.
